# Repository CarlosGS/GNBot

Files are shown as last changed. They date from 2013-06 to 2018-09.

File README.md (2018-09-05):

GNBot: robotic platform for cooperative search strategies
=====

Low-cost 3D-printable robot design for testing cooperative search algorithms.  

**Check [the GNBot wiki page](https://github.com/carlosgs/GNBot/wiki) for more information**  

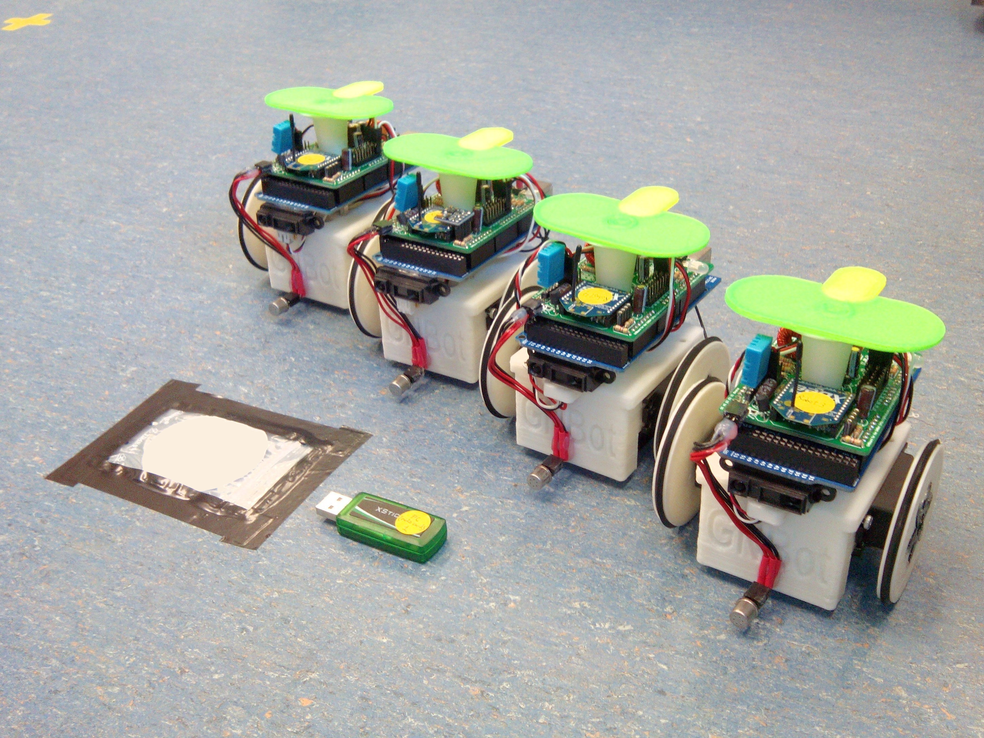
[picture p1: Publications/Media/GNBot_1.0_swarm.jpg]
  

The GNBot design allows the construction of a swarm of remotely-controlled robots that have multimodal sensory input (perceiving light, distance, temperature, humidity and orientation with an electronic compass) and are capable of detecting odor sources such as the low-profile target shown on the left.  

**Demonstration video of the swarm of GNBots used for Lévy-walk-based search:**
Demonstration video of the swarm of GNBots used for Levy-walk-based search (http://www.youtube.com/watch?v=HuAor0oZO_s)  

These robots are also energy efficient, open-source and easy to expand to allow the implementation of a great variety of cooperative search strategies (including those that use range information from each sensor modality with a characterization of the uncertainty of odor sources, and also the ones that use classical heuristic or brute-force approaches for search). Most importantly, the standardization of the platform could finally provide a fair base of comparison for evaluating differences in efficiency among these odor search strategies.  

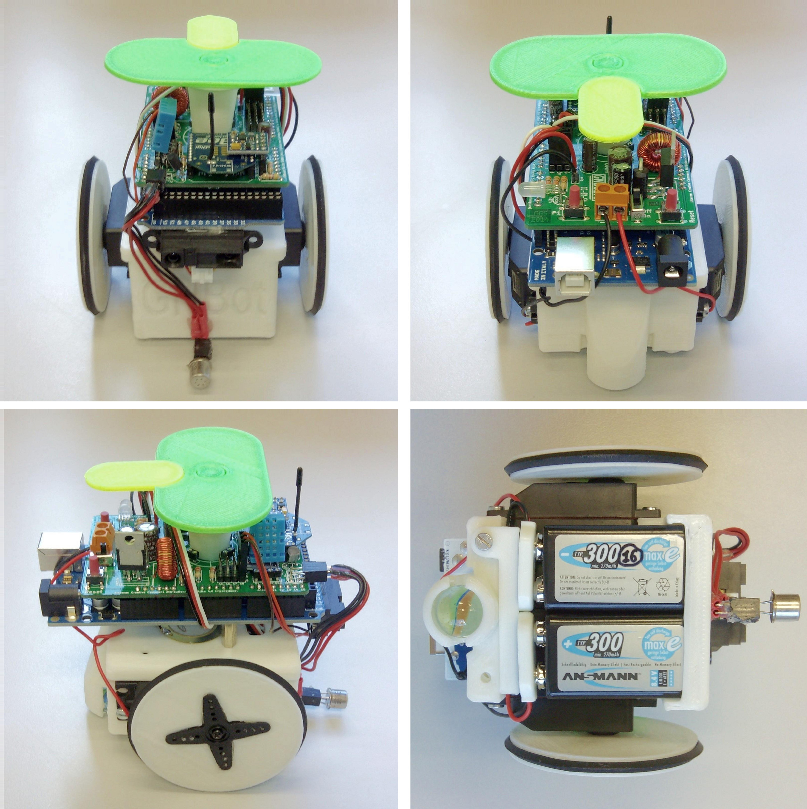
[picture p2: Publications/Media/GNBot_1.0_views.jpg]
  

List of sensors present in the robot:
TGS-2600 odor sensor, IR rangefinder, LDR light sensor array, electronic compass module, temperature and humidity sensors.
Battery voltage is also monitored.
The base actuators are two servomotors and the wireless interface is based on a ZigBee-compatible module.  

**Version 1.0:**  

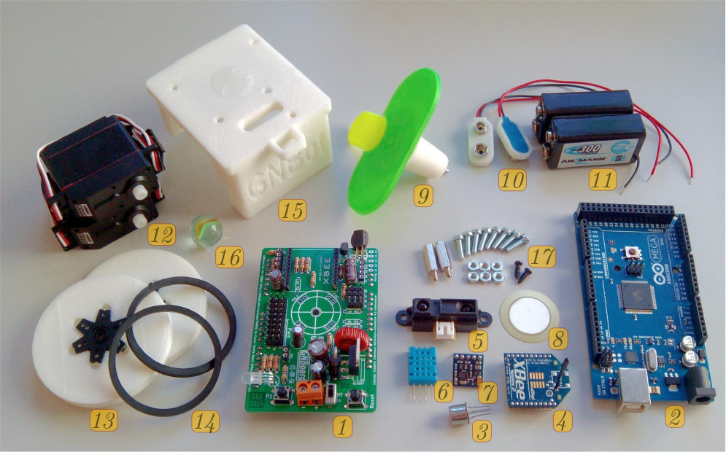
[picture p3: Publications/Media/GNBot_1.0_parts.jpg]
  

Items shown in the picture:
**1)** GNBoard electronics.
**2)** Arduino MEGA board.
**3)** TGS-2600 odor sensor.
**4)** ZigBee-compatible RF module.
**5)** Infra-red distance sensor.
**6)** DHT11 temperature and humidity sensor.
**7)** HMC5883L magnetometer sensor.
**8)** Piezoelectric buzzer.
**9)** Visual marker attachment.
**10)** Two 9V battery connectors.
**11)** Two 9V rechargeable batteries (300mAh).
**12)** Two continuous-rotation servomotors.
**13)** 3D-printed robot wheels.
**14)** Rubber outer-wheel rings.
**15)** 3D-printed GNBot chassis.
**16)** Marble for the idler wheel.  

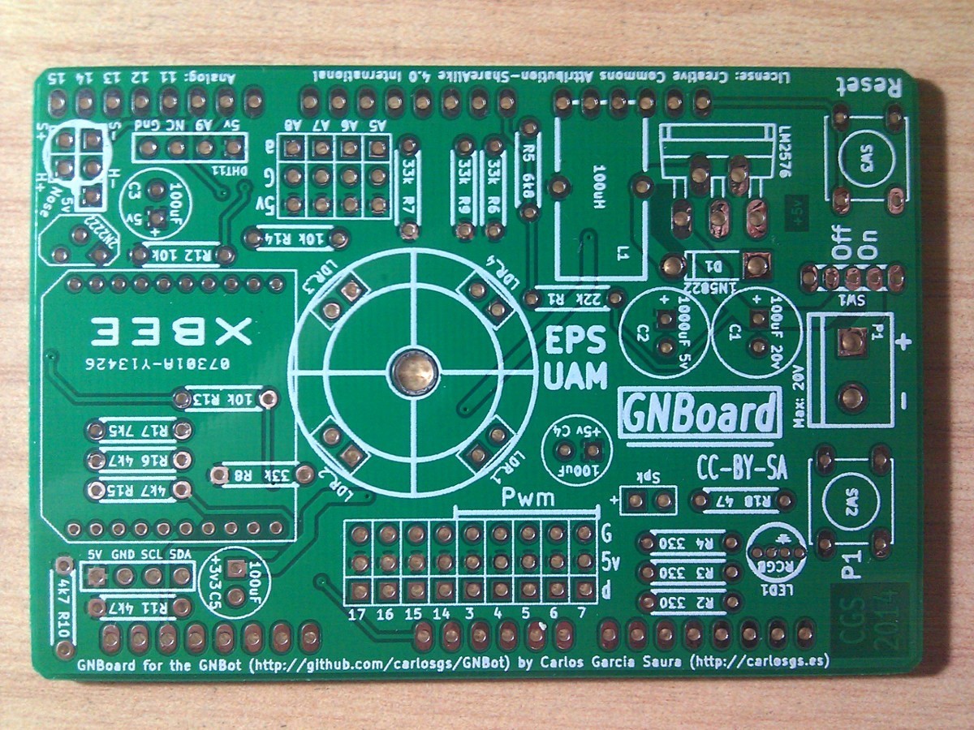
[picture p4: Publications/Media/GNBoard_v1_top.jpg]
  
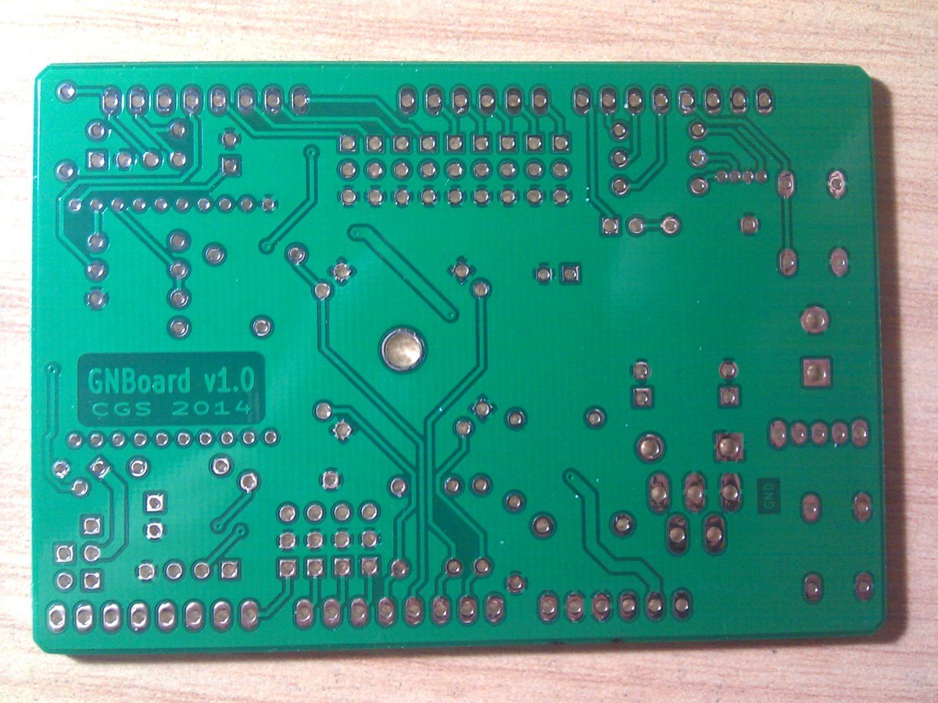
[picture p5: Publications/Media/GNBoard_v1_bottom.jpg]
  

**Version 1.0a:**  

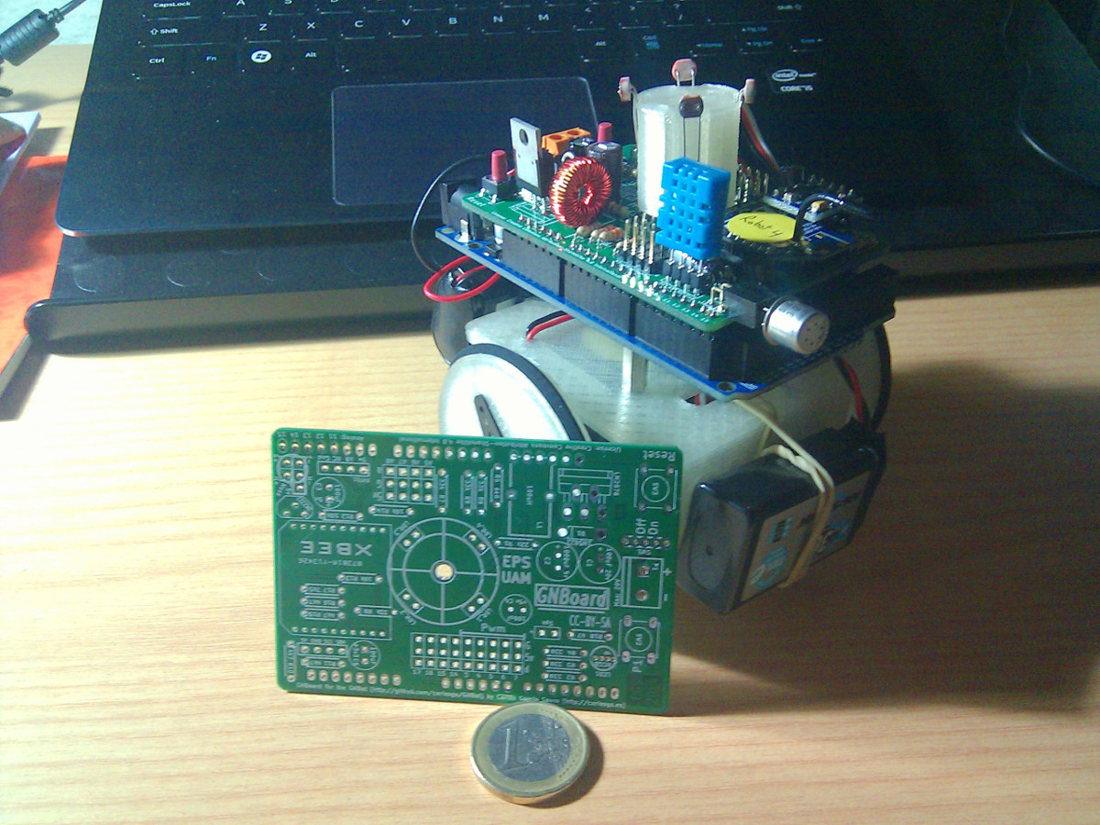
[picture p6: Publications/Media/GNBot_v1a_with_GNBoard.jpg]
  
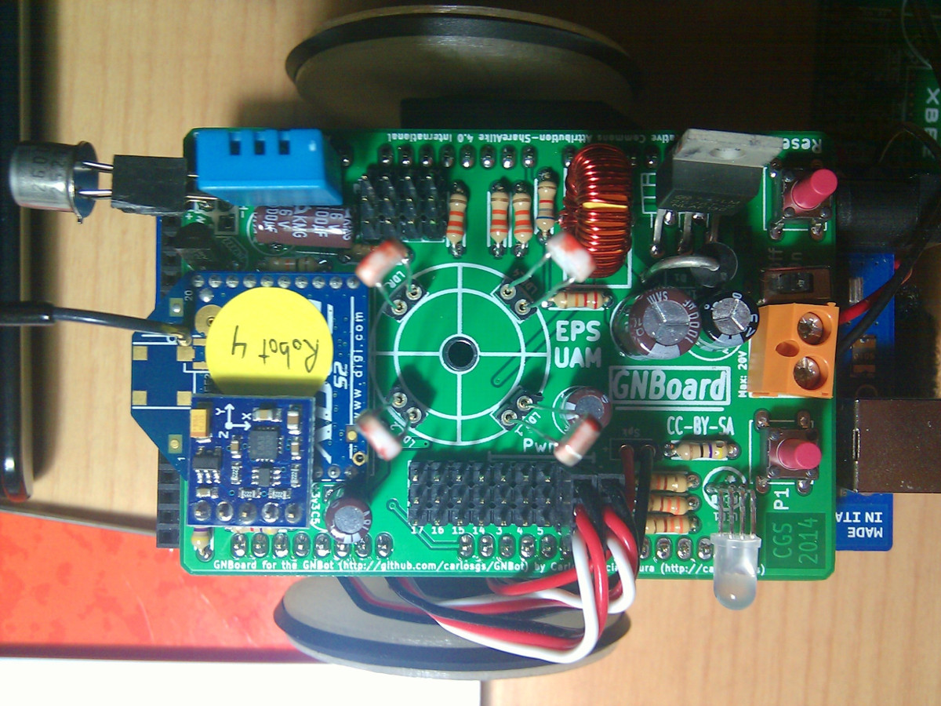
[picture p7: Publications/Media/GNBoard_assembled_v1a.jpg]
  

**Version 0.5:**  

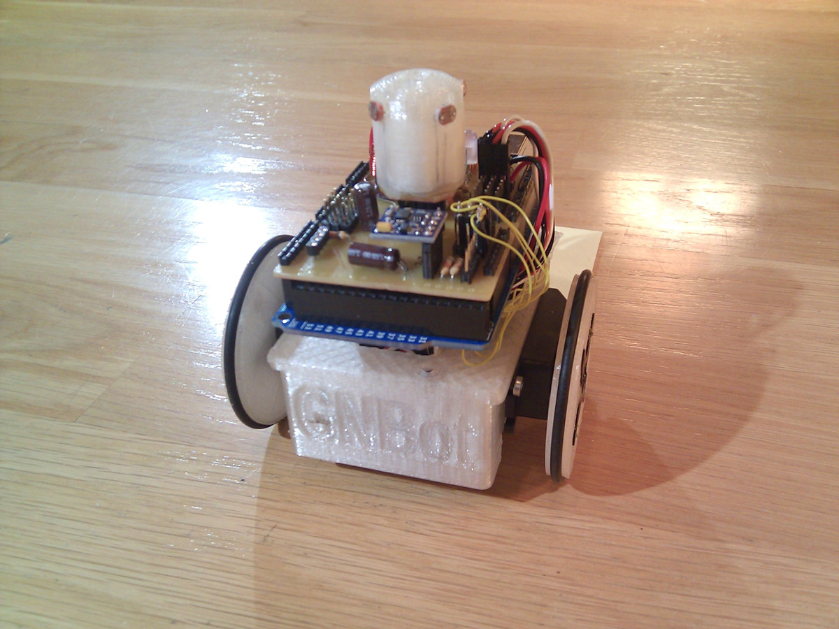
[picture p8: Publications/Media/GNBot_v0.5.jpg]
  

License  
--
License: **Attribution - Share Alike - Creative Commons (<http://creativecommons.org/licenses/by-sa/3.0/>)**  

Author:  
--
**@CarlosGS** <https://github.com/CarlosGS>

Disclaimer  
--
This hardware/software is provided "as is", and you use the hardware/software at your own risk. Under nocircumstances shall any author be liable for direct, indirect, special, incidental, or consequential damages resulting from the use, misuse, or inability to use this hardware/software, even if the authors have been advised of the possibility of such damages.

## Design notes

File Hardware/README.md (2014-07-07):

Hardware for the GNBot
=====

Designed derived from the ArduSkybot (whose origin was the MiniSkybot <http://www.iearobotics.com/wiki/index.php?title=Miniskybot_2>)

3d-printable robot design  
--

Regarding swarm robotics, printbots have been preferred over other solutions for both the reduced manufacture cost and, most importantly, for the high adaptability of the designs to the search problems. For instance, the use of 3D printed structures opens the possibility of easily testing the performance of various spatial distributions of the odor sensors in the robot, by manufacturing custom parts that can accommodate the different configurations.

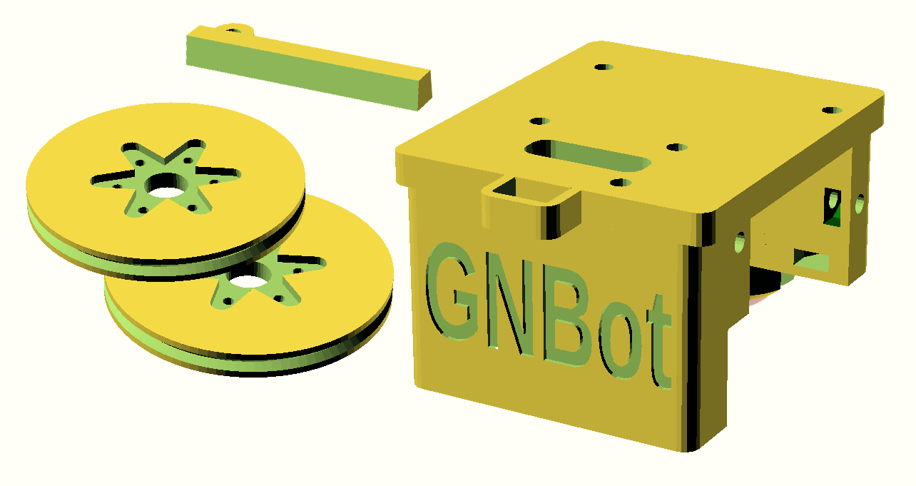
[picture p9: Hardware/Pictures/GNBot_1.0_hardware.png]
  

**Visual markers for video tracking with OpenCV**  
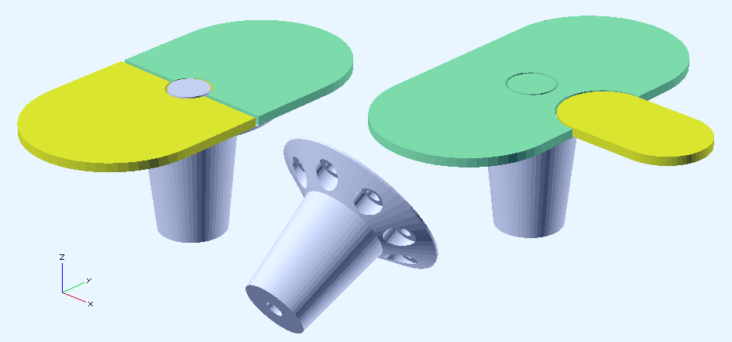
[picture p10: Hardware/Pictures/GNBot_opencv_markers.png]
  

License  
--
License: **Attribution - Share Alike - Creative Commons (<http://creativecommons.org/licenses/by-sa/3.0/>)**  

Author:  
--
**Carlosgs (<http://carlosgs.es>)**  

Disclaimer  
--
This hardware/software is provided "as is", and you use the hardware/software at your own risk. Under nocircumstances shall any author be liable for direct, indirect, special, incidental, or consequential damages resulting from the use, misuse, or inability to use this hardware/software, even if the authors have been advised of the possibility of such damages.

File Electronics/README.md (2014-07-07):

Electronics for the GNBot
=====

GNBoard shield for the Arduino MEGA  
--

An efficient solution for powering mobile robots. The GNBoard can also incorporate a ZigBee-compatible module and many other multimodal sensors (a gas detector for odor sensing, an accelerometer/electronic compass, temperature and humidity sensors, luminosity sensors), and multiple kinds of actuators as well (servomotors, a speaker, LEDs, etc).

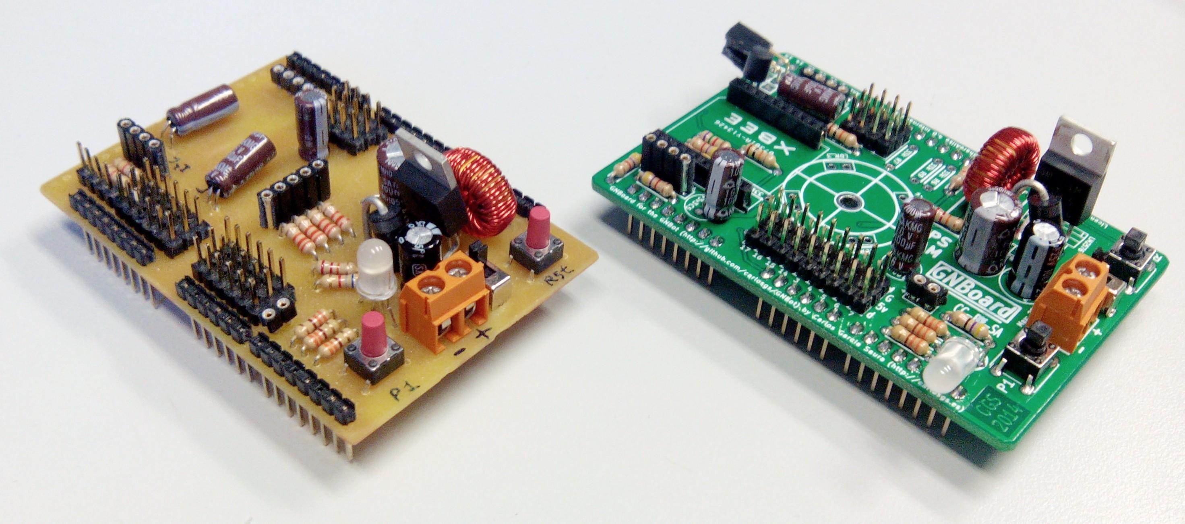
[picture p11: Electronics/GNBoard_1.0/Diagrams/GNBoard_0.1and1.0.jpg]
  
The two versions of the GNBoard developed for this project.
Prototype design (left) and version 1.0 (right).
The boards are designed to plug into an **Arduino MEGA**.  

The motion of the robot is achieved using two continuous rotation servomotors (**SM-S4303R**) as the main actuators. Servomotors provide a compact and low-cost solution to achieve the digital speed control needed.
The main downside of this kind of actuator is the high current demand -particularly during transient motions- which requires the use of an adequate power supply. For the GNBoard the design decision was to use a switching power supply rather than a linear regulator, provided the much higher efficiency.

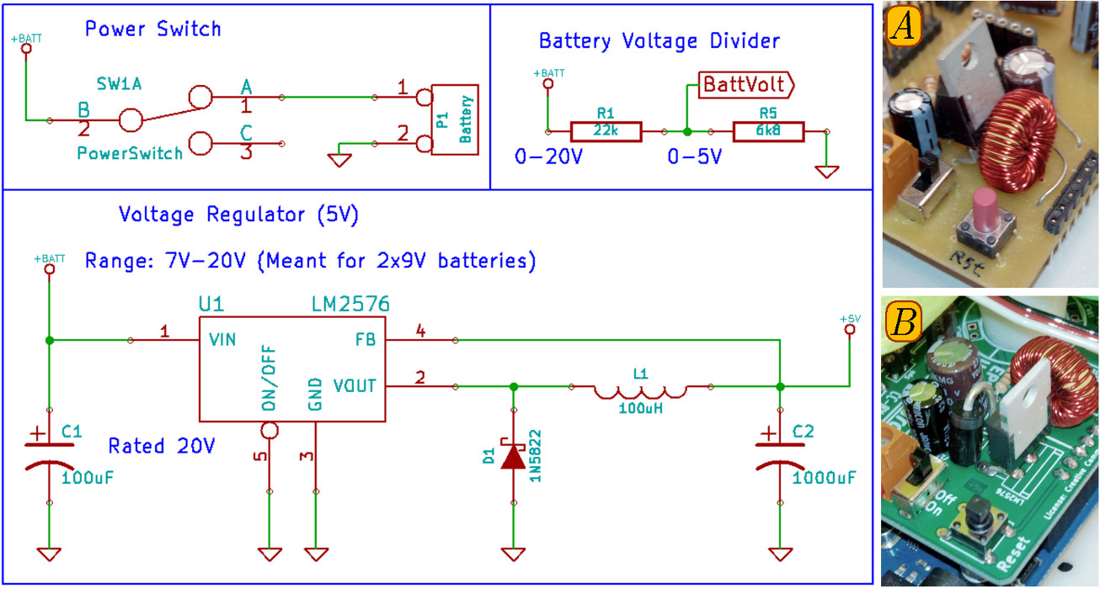
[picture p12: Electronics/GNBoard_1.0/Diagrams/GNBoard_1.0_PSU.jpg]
  
**Power supply schematic and actual assembly**
**A)** and **B)** respectively show the power supplies in GNBoard v0.1 and v1.0 (final version).
The power supply of the GNBoard uses an **LM2576-5** switching regulator that is capable of delivering up to 3A, which is more than sufficient to cover the energy demand of the entire robot.
Switching power regulators also have a broad input voltage range, allowing to make better use of the full capacity of the batteries since they can be connected in series without negative effect in the performance.

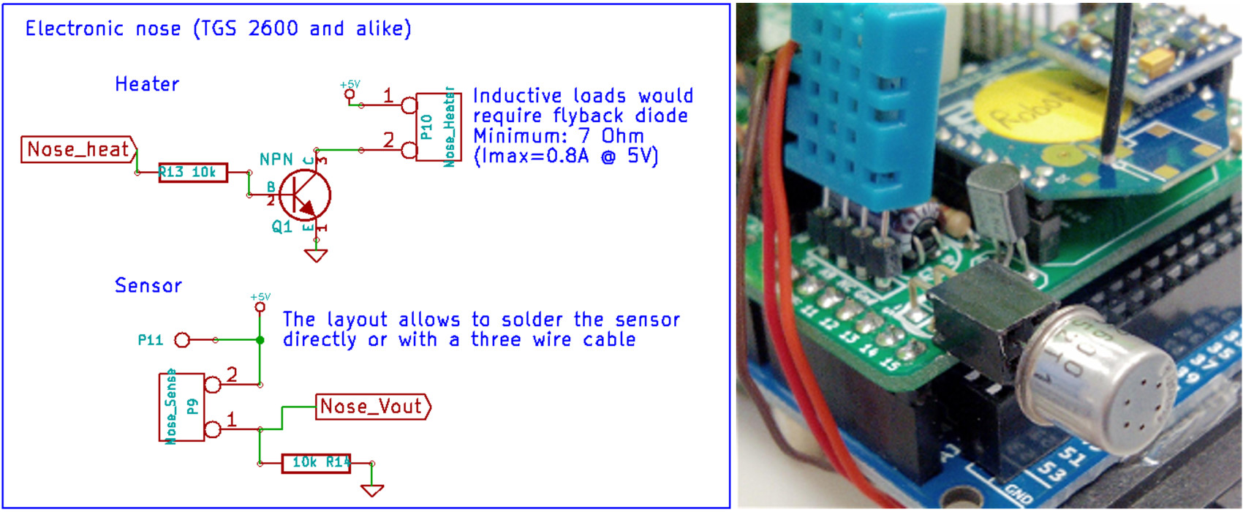
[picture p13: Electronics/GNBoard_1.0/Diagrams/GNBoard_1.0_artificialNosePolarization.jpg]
  
**Polarization scheme for the artificial nose sensor and detail picture of the assembly:**
The mounted sensor is the **TGS-2600** gas detector from <http://www.figarosensor.com/>, but any kind of sensor with a similar polarization scheme (as shown in the left panel) could be used.

Layout and schematics  
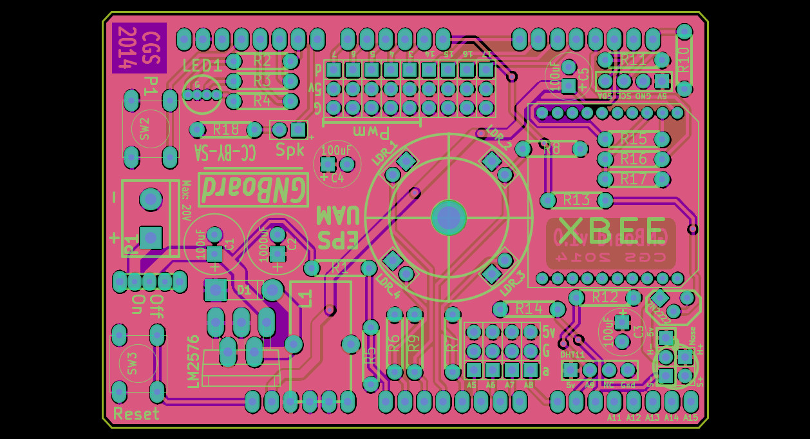
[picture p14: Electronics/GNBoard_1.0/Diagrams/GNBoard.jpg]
  
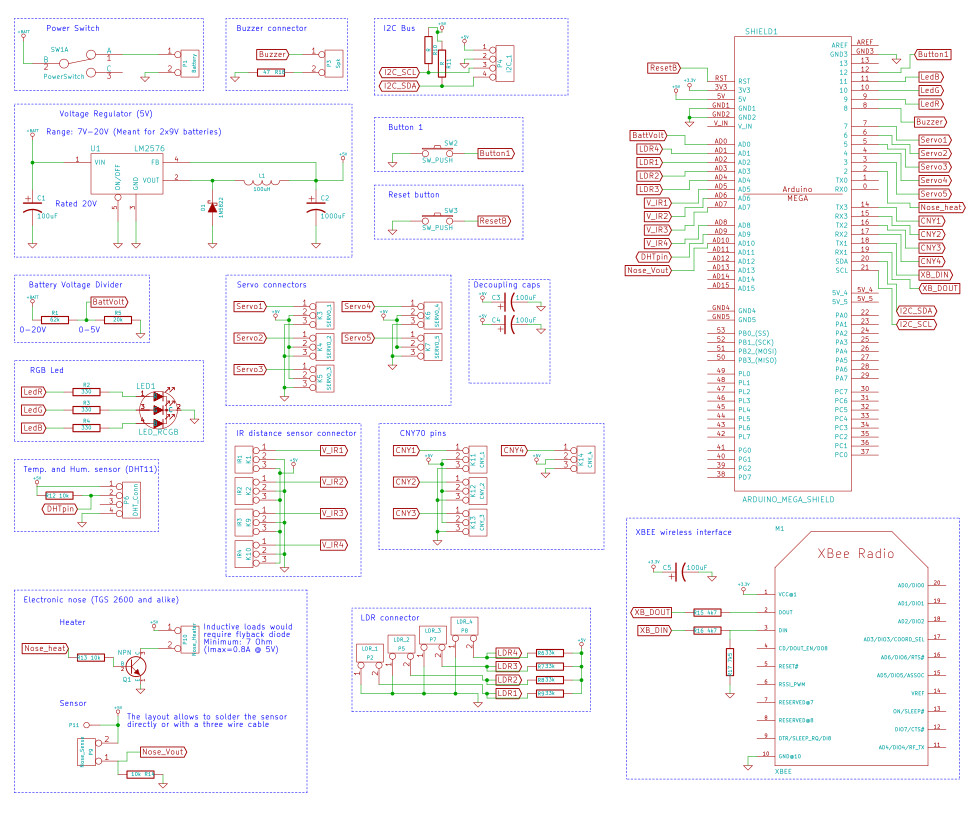
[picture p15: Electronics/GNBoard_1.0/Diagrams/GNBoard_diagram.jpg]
  
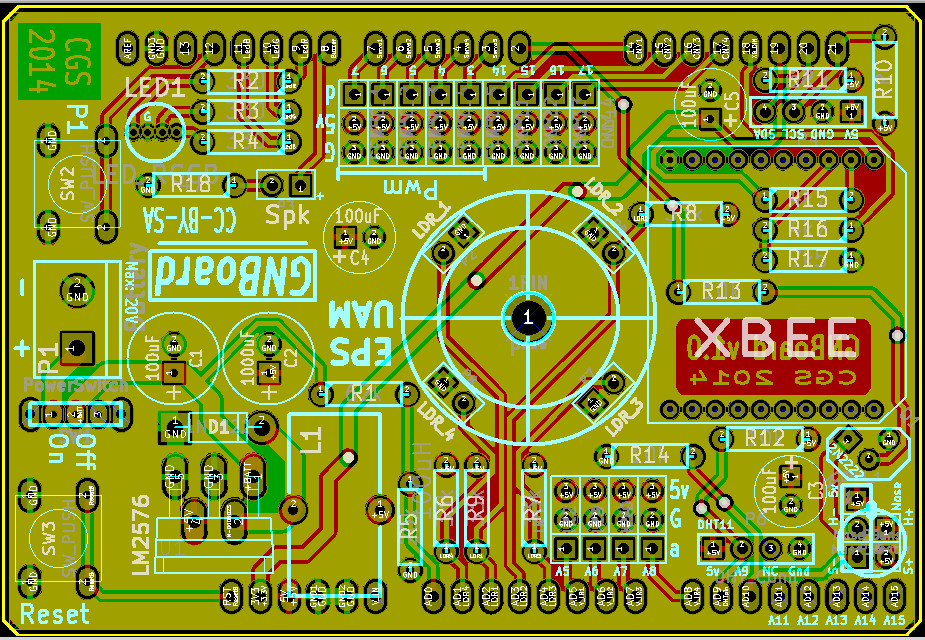
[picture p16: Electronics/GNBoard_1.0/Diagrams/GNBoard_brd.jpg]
  

License  
--
License: **Attribution - Share Alike - Creative Commons (<http://creativecommons.org/licenses/by-sa/3.0/>)**  

Author:  
--
**Carlosgs (<http://carlosgs.es>)**  

Disclaimer  
--
This hardware/software is provided "as is", and you use the hardware/software at your own risk. Under nocircumstances shall any author be liable for direct, indirect, special, incidental, or consequential damages resulting from the use, misuse, or inability to use this hardware/software, even if the authors have been advised of the possibility of such damages.

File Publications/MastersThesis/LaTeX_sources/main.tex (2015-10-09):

\documentclass[12pt,twoside]{report}

\usepackage{hyperref}
\hypersetup{
    hyperindex, linktoc=page, breaklinks,
    pdfauthor={Carlos Garcia-Saura},pdftitle={Self-calibration of a differential wheeled robot using only a gyroscope and a distance sensor}
}

\usepackage[utf8]{inputenc}
\usepackage{amsmath}
\usepackage{amsfonts}
\usepackage{amssymb}

\usepackage{setspace}

\usepackage{enumitem}

\usepackage[normalem]{ulem}

\usepackage[table,xcdraw]{xcolor}

%%%%%%%%%%%%%%%%%%%%%%%%%%%%%%%%%%%%%%%%%%%%%%%%%%%%%%%%%%%%%%%%%%%%%%%%%%%%%

% Definitions for the title page
\newcommand{\reporttitle}{Self-calibration of a differential wheeled robot using only a gyroscope and a distance sensor}
\newcommand{\reportauthor}{Carlos Garcia-Saura}
\newcommand{\supervisor}{Prof. Andrew J. Davison}
\newcommand{\degreetype}{Computing Science (Specialism in A.I.)}

\newcommand{\keywords}{Mobile robotics, differential wheeled robot, motion control, self-calibration, continuous-rotation servomotor, PID auto-tuning, multimodal sensing, MEMS gyroscope, IR distance sensor, open-source}

\setlength{\parskip}{\baselineskip}
\setlength{\parindent}{0pt}

%%%%%%%%%%%%%%%%%%%%%%%%%%%%%%%%%%%%%%%%%%%%%%%%%%%%%%%%%%%%%%%%%%%%%%%%%%%%%

% load some definitions and default packages
\input{includes}

\date{September 2015}

\begin{document}

% load title page
\input{titlepage}

\clearpage{\pagestyle{empty}\cleardoublepage}

% page numbering etc.
\pagenumbering{roman}
%\clearpage{\pagestyle{empty}\cleardoublepage}
\setcounter{page}{1}
\pagestyle{fancy}

%%%%%%%%%%%%%%%%%%%%%%%%%%%%%%%%%%%%
\begin{abstract}

Research in mobile robotics often demands platforms that have an adequate balance between cost and reliability. In the case of terrestrial robots, 
one of the available options is the GNBot, an open-hardware project intended for the evaluation of swarm search strategies.
The lack of basic odometry sensors such as wheel encoders had so far difficulted the implementation of an accurate high-level controller in this platform.
Thus, the aim of this thesis is to improve motion control in the GNBot by incorporating a gyroscope whilst maintaining the requisite of no wheel encoders.
Among the problems that have been tackled are: accurate in-place rotations, minimal drift during linear motions, and arc-performing functionality.
Additionally, the resulting controller is calibrated autonomously by using both the gyroscope module and the infrared rangefinder on board each robot, greatly simplifying the calibration of large swarms.
The report first explains the design decisions that were made in order to implement the self-calibration routine, and then evaluates the performance of the new motion controller by means of off-line video tracking. The motion accuracy of the new controller is also compared with the previously existing solution in an odor search experiment.

\textbf{Keywords:} \emph{\keywords}
\end{abstract}

\clearpage{\pagestyle{empty}\cleardoublepage}
%%%%%%%%%%%%%%%%%%%%%%%%%%%%%%%%%%%%
\section*{Acknowledgements}
\emph{In first place I must thank professor Andrew J. Davison at Imperial College London for his patient guidance and for pointing this project in the right direction.
I found the Robotics course to be very inspiring so I want to thank as well the rest of coordinators and course assistants.}

\emph{I am also thankful to professors Pablo Varona and Francisco de Borja Rodr\'iguez at Universidad Aut\'onoma de Madrid, for allowing me to use their infrastructure to perform the experiments. My friends Alejandro, Irene and Aar\'on also deserve a mention for making the research time in the lab (and outside the lab!) way more enjoyable.}

\emph{From the great people I have met this year at Imperial College London, I want to mention in special Hadeel, Bob, Matthew, Stefan, Marta, \sout{Dony}Doniyor, Pawel, Tony, Siwook, Yui, and Win for always being there, for the good and the bad, no matter how complicated the assignment or big the cake! :-)
I must mention as well the IC Robotics Society and IC Advanced Hackspace, in special Larissa and Audrey for helping a lot with the 3D printers and laser cutters.
Also, my year in London wouldn't have been the same without yOPERO, Erin, Charlaine, Christian and Cliona.}

\emph{I also want to thank the whole open-source community (specially GNU/Linux, Python, Numpy, Matplotlib, OpenCV, Arduino, RepRap, etc) for making it possible to perform this project without requiring any proprietary software or machinery.}

\emph{Finally, big thanks go to my parents for their continuous loving support, and also thanks to Rodrigo, FJ and Sandra for tolerating my mood swings while working in this project during our family holidays.}

\emph{!`Muchas gracias a todos!}

\emph{-- Carlos}

\clearpage{\pagestyle{empty}\cleardoublepage}

%%%%%%%%%%%%%%%%%%%%%%%%%%%%%%%%%%%%
%--- table of contents
\fancyhead[LE,RO]{\slshape}
\fancyhead[RE,LO]{\sffamily {Table of Contents}}

\begin{spacing}{0.1}
\tableofcontents 
\end{spacing}

\clearpage{\pagestyle{empty}\cleardoublepage}

\fancyhead[RE,LO]{\sffamily {List of Figures}}

\begin{spacing}{0.1}
\listoffigures
\end{spacing}

\clearpage{\pagestyle{empty}\cleardoublepage}
\pagenumbering{arabic}
\setcounter{page}{1}

\fancyhead[LE,RO]{\slshape}
%\fancyhead[LE,RO]{\slshape \rightmark}
\fancyhead[LO,RE]{\slshape \leftmark}

%%%%%%%%%%%%%%%%%%%%%%%%%%%%%%%%%%%%
\chapter{Introduction}

The starting point of this project is the \emph{GNBot} swarm robot platform that was presented in \emph{``Design principles for cooperative robots with uncertainty-aware and resource-wise adaptive behavior''}\cite{GarciaSauraLM14}, and \emph{``Cooperative strategies for the detection and localization of odorants with robots and artificial noses''}\cite{GarciaSaura14}.
Figure \ref{fig:GNBotViews} describes the most relevant characteristics of these robots.

\begin{figure}[hbtp]
\centerline{
}
\caption[One of the robots from the GNBot swarm used for the project]{\emph{One of the robots from the GNBot swarm used for the project.}
The electronics are based on the Arduino MEGA board. A custom shield contains all of the multimodal sensors, which provide the robot with gas sensing capabilities (TGS-2900), as well as distance sensing (GP2Y0A21YK0F), temperature \& humidity (DHT11), and light intensity sensing.
\textbf{This project additionally incorporated a gyroscope module (MPU6050)}.
The main actuators are two continuous-rotation servomotors, and each robot also has a multicolor RGB LED and a piezoelectric speaker.
Finally, the wireless communication layer is based on ZigBee, and the green/yellow top markers allow for external video tracking of the swarm.
From \cite{GarciaSauraLM14,GarciaSaura14}.
}
\label{fig:GNBotViews}
\end{figure}

The GNBot is a \emph{differential wheeled robot}, which means that it has two active wheels sharing the same axis, and each of them is actuated independently. There is also a passive, free turning ball caster that acts as a third stand. If the desired trajectory is a straight path, the velocities are set to equal magnitude; if a rotation is required instead, then different velocities can be applied to each motor.

Using this setup it is possible to estimate the motion of the robot in the XY plane given its starting position ($P_{xy\alpha}$), the rotational velocity of each motor ($\omega_L$, $\omega_R$), the diameter of the wheels ($D_L$, $D_R$) and their separation ($d$). This estimation process is known as \emph{dead reckoning}\footnote{\url{https://en.wikipedia.org/wiki/Dead_reckoning}}.

The accuracy of dead reckoning relies on how dependable the measurements used in the calculations are. These include wheel separation and their diameter, but most importantly the actual rotational velocities of each motor.
For instance, small deviations from the theoretical velocities can turn a desirably linear trajectory into an arc. An example of this issue is displayed in Figure \ref{fig:levyDriftSingle}.

\begin{figure}[hbtp]
\centerline{
}
\caption[Example of an odor search strategy based on L\'{e}vy walks, as performed by the original robot controller]{\emph{Example of an odor search strategy based on L\'{e}vy walks, as performed by the original robot controller.}
The search is defined at a high level as random in-place rotations combined with linear trajectories whose lengths vary according to a heavy-tailed probabilistic distribution. \textbf{It can be appreciated that the segments that were supposed to be linear, are actually performed as arcs (there is drift in yaw)}.
In this experiment, the target odor source (red marker) took 12 minutes to be found.
The ground truth trajectory was recorded with a webcam, post perspective correction and color marker tracking with the OpenCV software library.}
\label{fig:levyDriftSingle}
\end{figure}

\pagebreak

This thesis has tackled the improvement of those low-level control routines in order to minimize motion drift, as well as the implementation of a distance-based abstraction layer that facilitates the use of the GNBot platform in practical applications.
It also explores the automatic calibration of the robots using only on-board sensors (a gyroscope and a distance sensor).

The following two sections are an overview of the project's approach towards the improvement the motion controller; Chapter \ref{sec:calib_chap} provides an in-depth explanation of the self-calibration algorithm; Next, Chapter \ref{sec:eval_chap} evaluates the resulting controller; Finally, Chapter \ref{sec:concl_chap} analyses the outcome of the project and suggests future research paths.

\section{Background and motivation} \label{sec:bg_section}

Undesired drift in the estimation of position, very characteristic when using dead reckoning in mobile robotics, can be reduced with the incorporation of basic \emph{odometry}\footnote{\emph{Odometry:} Use of sensory data to improve motion estimates} such as \emph{rotational encoders}\footnote{\emph{Rotational encoder:} A sensor that can measure wheel rotations accurately and in real time}.
Wheel encoders are a very common choice given their simplicity and reduced cost, but they do have some drawbacks:
\begin{itemize}[noitemsep,topsep=0pt,parsep=5pt,partopsep=0pt]
\item Incorporating wheel encoders into a previously existing design is often nontrivial, as the process involves hardware modifications  near critical moving parts.
\item Electrical, optical or magnetic wheel encoders can be susceptible to dirt; placing them near the wheels may make periodic maintenance necessary.
\item Most importantly, wheel encoders cannot easily detect whether there is any slipping between the wheel and the ground surface.
\end{itemize}

For these reasons the incorporation of wheel encoders in the GNBot has been dismissed.
Instead, the first trials towards the reduction of yaw drift included the use of an electronic compass. The goal was to obtain a global, unbiased measure of heading (yaw) by measuring the earth's magnetic field. Unfortunately the compass was deemed unusable for indoor environments during the first trials of the GNBot\cite{GarciaSaura14}, since the magnetometer measurements are substantially distorted by nearby metals (i.e. buried cables) commonly present indoors.

Another option for odometry is the gyroscope, which is the approach studied in this project (see Fig. \ref{fig:GNBotGyro}). Electronic gyroscopes are a form of inertial sensor that can measure relative rotations in any orientation, without requiring interactions with external moving parts. As opposed to wheel encoders, the physical incorporation of a gyroscope into the GNBot would be quite straightforward, and would also have the advantage of being capable of easily detecting wheel slipping.

\begin{figure}[hbtp]
\centerline{
}
\caption[Detail of the gyroscope module installed in the GNBot]{\emph{Detail of the gyroscope module installed in the GNBot.} The selected board is based on the MPU6050 module, which is Arduino-compatible. The module fits on the $I^2C$ socket of the GNBot without any additional modification.
An orange wire was soldered to the interrupt pin, but it was not needed in the end, as polling was used to read values from the module.
}
\label{fig:GNBotGyro}
\end{figure}

The use of inertial sensors for position estimation has been a matter of research for many decades. The last few years in particular have seen the development of smartphones, tablets, intelligent cameras and other devices in need of inertial sensors, which has greatly boosted the industry. The technology has been able to achieve high miniaturization, high accuracy and low power consumption, whilst substantially reducing costs, yielding the excellent inertial sensors that are now widely available in the market.

In robotics, Inertial Measurement Units (IMUs) are quite often employed for navigation in different environments.
For instance, the combination of IMUs with GPS allows for a remarkably accurate 3D localization in aerial robotics\cite{Barczyk10}. These techniques have also been demonstrated in ground robots without GPS\cite{PeiChunLin06,SeungbeomWoo11}, as well as in underwater robots without encoders\cite{Stilwell01,Kinsey02,Panish11}.
More recently, 3D position tracking with inertial sensors has also been employed to correct the effect of the rolling shutter of RGB\cite{HyoungKiLee12} and RGB-D\cite{Ovren13} camera sensors.

Many authors use \emph{Kalman filters}\footnote{\url{https://en.wikipedia.org/wiki/Kalman_filter}} in their motion controllers. Kalman filtering is a probabilistic method for sensor fusion, which means it can be used to efficiently combine measurements from the inertial sensor with other forms of odometry such as wheel encoders, a compass, or even barometers; this way it is possible to achieve very robust motion controllers with minimal drift\cite{PeiChunLin06,HyoungKiLee12,
HakyoungChung01,panich11}.
In fact, most of the commercially-available IMUs, such as the one selected for this project, already contain internal Kalman filters that can integrate measurements from a gyroscope, an accelerometer or a compass.

For the final evaluation of the positioning accuracy of the controller, the project took advice from work by J. Borenstein et al.\cite{HakyoungChung01,Borenstein98}, where the robots were programmed to describe square trajectories that were first logged and then compared against ground truth.

%Self calibration (SLAM):
%\cite{DeCecco02} % inertial + odometry
%\cite{roy99}
%\cite{martinelli07}

%kalman
%\cite{HakyoungChung01,PeiChunLin06,
%HyoungKiLee12,martinelli07,panich11}

%Gyro. Square for evaluation:
%\cite{Borenstein98,HakyoungChung01}

%3D navigation (including accelerometers):
%Inertial navigation systems:
%Hexapod:
%\cite{PeiChunLin06}
%UAV aided by GPS:
%\cite{Barczyk10}
%Linear velocity calibration using Fuzzy %inference:
%\cite{SeungbeomWoo11}

%Monocular SLAM:
%\cite{HyoungKiLee12}

%RGB-D rolling shutter:
%\cite{Ovren13}

%Gyro. Underwater:
%\cite{Stilwell01,Kinsey02,Panish11}

%Gyro. Kalman filter
%\cite{panich11}

\section{Contribution overview}

At the start of this project, the motion control of the GNBot robots was speed-based and open-loop (with no wheel encoders). This resulted in very inaccurate motions that drifted rapidly from the desired path. For example, when a robot was commanded to describe a straight trajectory, an arc path would be observed instead. In-place rotations were also quite inaccurate.

Thus the goal of this project has been to improve the motion accuracy of these robots and to provide a high-level distance-based controller.
In particular the following matters have been tackled:

\begin{itemize}
\item Incorporation of an inertial sensor (MPU6050) into the GNBot design, as well as the implementation of low-level functionality that reads \emph{yaw, pitch and roll} from the gyroscope module with minimal drift.
\item Analysis of the servomotor response curves. Since there are no wheel encoders, the rotations were tracked using the gyroscope, by independently rotating each wheel over the entire range of velocities.
\item Implementation of a PID controller for accurate yaw regulation; Additionally the constants are auto-calibrated with a process based on the Ziegler-Nichols method.
\item Analysis of the infrared sensor response curve, and linearisation using exponential curve fitting.
\item Analysis of the nonlinear effect of the PID yaw controller over the robot's linear velocity for the whole range.
\item The results of these analysis have been integrated into a high-level distance-based motion controller that supports linear motions and arcs. Additionally, the calibration of each robot is done autonomously by using only on-board sensors (the gyroscope and the IR rangefinder) and requiring minimal user interaction.
\item Implementation of an off-line video tracking method capable of reliably recording ground truth robot paths. The process involved perspective \& distance correction using the OpenCV library.
\item Evaluation of the new controller by making the robots perform lines, circles and squares of known dimensions; Also the system was compared against the previously existing solution in an odor search task based on a wall-bounce strategy.
\end{itemize}

The new motion controller has a linear drift in the order of $6cm/m$ in the low velocity settings ($2$ to $6cm/s$) and around $9cm/m$ at higher velocities ($6$ to $10cm/s$). The rotational drift is in the order of $2deg/min$ when the robot is moving.

In summary, this project has provided the high-level functionality needed in order to achieve accurate control over the GNBot robots. The self-calibrating nature of the approach also facilitates its use in large robot swarms.

The outcome of the project is open-source (Attribution-ShareAlike 4.0 International\footnote{\url{http://creativecommons.org/licenses/by-sa/4.0/}}) and can be accessed in the following GitHub respository:

\begin{center}
\large\url{https://github.com/carlosgs/GNBot}
\end{center}

%%%%%%%%%%%%%%%%%%%%%%%%%%%%%%%%%%%%
\chapter{The self-calibration algorithm} \label{sec:calib_chap}

The original controller on-board the GNBot was velocity-based and its input units were arbitrary -- it did not have an internal mapping between the motor's inputs and real-world units (i.e. $cm/s$). It was also lacking methods for basic calibration, in part due to the absence of any form of odometry. Altogether, these facts lead to large amounts of drift.
Far from being a constant that could have been compensated by basic calibration, drift varied with the velocity of the robots -not only in magnitude but also in direction-, so straightforward calibration was not an option (see Figure \ref{fig:gnbotLinearDrift}).
This project has tackled the problem by incorporating a gyroscope for odometry. The advantages of this approach in contrast with the use of wheel encoders were already discussed in Section \ref{sec:bg_section}.

The selected \emph{Inertial Measurement Unit} (IMU) is the MPU6050\footnote{\url{http://www.invensense.com/products/motion-tracking/6-axis/mpu-6050/}} chip, which is based on MEMS technology (Micro-Electro-Mechanical Systems). It is commonly available as an Arduino-compatible break-out board that conveniently fits on the $I^2C$ socket of the GNBot without any additional modifications (c.f. Figure \ref{fig:GNBotGyro}).

The gyroscope module has the same $I^2C$ pinout as the magnetometer that was originally present in the robot, but the routines that handle both modules are very different. In fact, the example code for the inertial sensor (a part of the \emph{$I^2C$ Device Library}\footnote{\url{http://www.i2cdevlib.com/devices/mpu6050}}) depends on the use of hardware \emph{interruptions}\footnote{\emph{Interrupt:} Signal to the processor indicating that some event needs immediate attention} rather than \emph{polling}\footnote{\emph{Polling:} As opposed to interruptions, polling actively samples the status of an external device}.
The use of interruptions was highly undesirable since the main processor needs to handle time sensitive tasks such as sensing and radio communications as well as motion control, so the gyroscope library was modified to use a polling scheme.

The MPU6050 incorporates a \emph{Digital Motion Processor} (DMP) that can be used to offload computations from the robot's main processor. These computations include the task of filtering and integrating the raw values from the on-chip acceleration sensors, in order to output ready to use \emph{yaw, pitch and roll}. In the GNBot controller the raw values are sampled and processed at $200Hz$ by the DMP co-processor.

The gyroscope module also has an internal FIFO\footnote{\emph{FIFO:} ``First In First Out'' queuing policy} buffer that allows for reliable high-frequency data readings (up to $200Hz$), though in this project it was deemed unnecessary since the sample rate is low ($<50Hz$). Once the IMU had been incorporated into the GNBot, it was possible to read the \emph{yaw, pitch and roll} of the robot back into the computer (see Figure \ref{fig:gnbotLinearDrift}).

\begin{figure}[hbtp]
\centerline{
}
\caption[Initial experiments to analyse drift in the original controller]{\emph{Initial experiments to analyse drift in the original controller.} The robot was commanded to describe a straight path by setting both motors to the same velocity during 3 seconds.
The trajectory (upper panel) was recorded with a ceiling camera for three different velocities, while yaw (lower panel) was being logged using the on-board gyroscope.
It can be observed that drift is accurately tracked by the empirical yaw measurements.
The input speed setting is arbitrary since both continuous-rotation servomotors are commanded with the built-in $Servo.write([degrees])$ functions from the Arduino IDE, which do not have a direct mapping with real world velocities.
}
\label{fig:gnbotLinearDrift}
\end{figure}

At this point, a basic proportional yaw controller was implemented in order to demonstrate the viability of the system. The controller could now successfully correct the direction of the robot so it followed a straight path, even after external perturbations had been applied (i.e. rotating the robot or placing obstacles).

With those results as a motivation, the design of a high-level self-calibrating motion controller was tackled. An overview of the resulting calibration routine is shown in Figure \ref{fig:full_calibration_procedure} -- Further sections will describe the technical details in greater depth.

\begin{figure}[hbtp]
\centerline{}
\caption[Full self-calibration procedure]{\emph{Full self-calibration procedure.} \textbf{\textit{(a)}} The robot is first placed in front of a wall, and remains static while the gyro drift is compensated, \textbf{\textit{(b)}} The minimum motion threshold is found by gradually increasing the input of each motor until a rotation is perceived \textbf{\textit{(c)}} The motors are then independently run at their maximum speed setting in order to record the corresponding real-world rotational velocity, \textbf{\textit{(d)}} Next, the yaw PID controller is heuristically calibrated by analysing the oscillations for different parameters, \textbf{\textit{(e)}} Finally, the robot uses the distance sensor to measure its approach velocity towards the wall, creating a map between the input values ($rad/s$) and the resulting real-world linear velocity ($cm/s$).\\
Technical details can be found in sections: $(a)$ \ref{sec:gyro_section}, $(b$ \& $c)$ \ref{sec:rotVel_section}, $(d)$ \ref{sec:PID_section}, $(e)$ \ref{sec:linearVel_section}.
}
\label{fig:full_calibration_procedure}
\end{figure}

\newpage
\section{Minimization of gyroscope drift} \label{sec:gyro_section}

Most electronic gyroscopes calculate rotational magnitudes by integrating measurements from rotational accelerometers over time.
Ideally this integration process would consistently yield the same outputs when a sequence of rotations is applied, but instead, rotational accelerometers often have inaccuracies (i.e. bias, sensitivity limits, variability with temperature, etc.) that cause \emph{drift} in the integration process.
This would imply for instance that the yaw measurement of a static robot would erroneously vary over time.

Gyroscope drift is often minimized with either a proper calibration of the accelerometer bias, with signal filtering or by pausing the integration process while no motion is detected. Fortunately, the DMP co-processor of the MPU6050 already implements these features very efficiently (see Fig. \ref{fig:gyro_drift}).

In order to measure yaw drift rate (whose units are \emph{degrees per minute}) it was necessary to differentiate the yaw measurements provided by the gyroscope (\emph{radian} units). This was achieved by accurately timing distinct yaw measurements with the function \emph{millis()} from Arduino\footnote{\url{https://www.arduino.cc/en/Reference/Millis}}.
\begin{equation}
drift\_rate=\frac{yaw(t_2)-yaw(t_1)}{t_2-t_1}\cdot\frac{180 deg}{\pi rad}\cdot\frac{1 min}{60 s}deg/min
\end{equation}

\vspace{-5mm}

\begin{figure}[hbtp]
\centerline{
}
\caption[Analysis of gyroscope drift (with static robot)]{\emph{Analysis of gyroscope drift (with static robot).} The gyroscope has an initial transient that must be respected, during which the internal DMP (Digital Motion Processor) performs self-calibration to account for drift. The module is fully calibrated after 23 seconds of the robot being static, when drift becomes inferior to 0.5 deg/min (step A in Fig. \ref{fig:full_calibration_procedure}). It must be noted though that the magnitude of this drift will not be constant, but is instead greatly affected by the robot's motions.
}
\label{fig:gyro_drift}
\end{figure}

\section{Calibration of the motors} \label{sec:rotVel_section}

This section tackles the calibration of the continuous-rotation servomotors, which are actuators that generate a rotational velocity that is proportional to a PWM input signal (Pulse Width Modulation).
The relationship between the input and output magnitudes is arbitrary, so a real-world mapping needs to be learned first.

To better understand the calibration process it helps to be familiar with the following notation:

\begin{figure}[hbtp]
\centerline{
}
\caption[Diagram of the robot's top view, displaying the notation used]{\emph{Diagram of the robot's top view, displaying the notation used.}
The grey arrow points towards the front of the robot.
$D_L$ and $D_R$ are the wheel diameters, and $d$ is their separation. $V_L$ and $V_R$ are the contributions of each motor to the robot's linear velocity, and $\alpha$ is the yaw measurement (positive for clockwise rotations).
}
\label{fig:robot_diagram_notation}
\end{figure}

Most mobile robotic platforms have encoders that simplify the calibration process by measuring the real-world rotational velocities of the wheels. In the case of the GNBot there are no wheel encoders, so a different approach was needed.

The implemented method can measure the response curve of each motor independently by using only the gyroscope. This process is described in Figure \ref{fig:speed_calib_diagram}.

\begin{figure}[hbtp]
\centerline{
}
\caption[Method employed to measure $\omega_R$, the contribution of the right motor to the robot's rotational velocity $\omega$.]{\emph{Method employed to measure $\omega_R$, the contribution of the right motor to the robot's rotational velocity $\omega$.}
A constant velocity is first applied to the right wheel ($V_R=C$) while the left wheel is fixed ($V_L=0$).
This results in a rotation of the robot around the ground-contact point of the left wheel. The gyroscope is then used to measure the rotational velocity $\omega_R=\omega$.
Afterwards the same process is repeated for the left motor.
This method allows to separately evaluate the response curves of each motor without requiring wheel encoders.
}
\label{fig:speed_calib_diagram}
\end{figure}

The angular velocity $\omega$, directly measured by the gyroscope, is coupled with the rotational speed of both motors with constants $K_L$ \& $K_R$, that account for $D_L$, $D_R$ (wheel diameters), and $d$ (distance between wheels).
Using this technique it was possible to record the response curve of each motor by independently performing a sweep over the full range of velocity inputs.
The result is shown in Figure \ref{fig:velocity_response_curve}.

\begin{figure}[hbtp]
\centerline{
}
\caption[Measured motor response curves]{\emph{Measured motor response curves.}
The panels show the response curves of the left (red) and right (blue) motors for different wheel sizes.
The input of the continuous-rotation servomotors is PWM (Pulse Width Modulation), and the output ($\omega$) is the rotational rate of the robot around its vertical axis (the setup is described in Fig. \ref{fig:speed_calib_diagram}).
Each trial was run for a single motor at a time, and the sweep took around 30 seconds per motor.
Three regions can be appreciated: a flat \emph{dead-zone} ($\omega=0rad/s$), a linear response region ($0 < \omega < 1.5rad/s$), and saturation ($\omega \geq 1.5rad/s$, which has been highlighted in red).
For the same wheel size -middle panel- the L/R response curves are almost identical.
Robots with larger left or right wheels -left \& right panels- instead have visibly different L/R response curves.
The calibration routine implemented in this project accounts for these differences.
}
\label{fig:velocity_response_curve}
\end{figure}

Self-calibration of these curves has been implemented by means of linear fitting between the minimum and maximum velocities within the linear region. In first place, the robot measures the \emph{dead-zone} of a motor (the minimum motion threshold) by gradually increasing its input velocity until a rotation is perceived. Then, the maximum velocity is measured by running the motor at the maximum speed setting within the linear range (PWM$\approx$1300 or PWM$\approx$1650).
These measurements are performed for the forward and backward directions of each motor (steps B \& C in Fig. \ref{fig:full_calibration_procedure}).

The left and right motors contribute to the robot's global angular velocity $\omega$ in an additive manner ($\omega=\omega_L+\omega_R$, i.e. setting $\omega_L=0.5rad/s$ and $\omega_R=0.5rad/s$ yields $\omega=1.0rad/s$).
Knowing this fact, and using the data from Figure \ref{fig:velocity_response_curve}, it was possible to determine the input region that corresponds to a linear motion. This is when both rotational contributions cancel out so the robot does not rotate: $\omega=\omega_L+\omega_R=0rad/s \rightarrow \omega_L=-\omega_R$.
This region is represented in Figure \ref{fig:linear_trajectory_PWM_mapping}.

\begin{figure}[hbtp]
\centerline{
}
\caption[Region of motor input values that correspond to a linear trajectory]{\emph{Region of motor input values that correspond to a linear trajectory.}
The red and green data points are from robots with larger left or right wheels respectively, while the blue data points are from a robot with identical wheels. It can be observed that each of these curves has a different steepness: a greater slope indicates that the right motor needs to rotate faster in order to account for a larger left wheel, and vice-versa.
}
\label{fig:linear_trajectory_PWM_mapping}
\end{figure}

\section{PID auto-tuning using the Ziegler-Nichols method} \label{sec:PID_section}

At this point a basic motor controller had been implemented, so the rotational rate ($rad/s$) of the robot could be accurately commanded. Closed-loop yaw control was now possible with the implementation of a PID regulator (Proportional-Integral-Derivative) that combines the  motor controller with real-time gyroscope measurements (Eqn. 2.2). The error measure is calculated as $e(t)=yaw_{target}-yaw(t)$.
\begin{equation}
output\_rotation\_rate(t) = K_p e(t) + K_i \int_{0}^{t}e(\tau)d\tau + K_d \frac{d}{dt}e\ \ [rad/s]
\end{equation}

A PID controller is based on user-tunable gains ($K_p$, $K_i$ \& $K_d$) that, when properly adjusted, can minimize the overshoot of the transient response; in the case of the GNBot, the PID is the responsible of achieving fast and accurate changes in yaw. This is represented in Figure \ref{fig:P_controller_vs_autotuned_PID}.

\begin{figure}[hbtp]
\centerline{}
\vspace{-3mm}
\centerline{}
\caption[Response of the yaw controller to a step function and to a sinusoid]{\emph{Response of the yaw controller to a step function (upper panel) and to a sinusoid (lower panel).}
The controller was commanded with time-varying yaw targets while the transitions were recorded using the gyroscope.
It can be appreciated that a proportional controller either is too slow (cyan curve), has over-shoot (blue curve) or even ripple (red curve).
The auto-tuned PID (green curve) does have some overshoot as well, but it is a much better approximation to the ideal response.
}
\label{fig:P_controller_vs_autotuned_PID}
\end{figure}

Rather than manually specifying a fixed parameter set for the PID, this project tackled the self-calibration of the controller with the popular technique proposed by Ziegler and Nichols\cite{ziegler1942optimum}. This heuristic tuning method is performed by setting the three gains ($K_p$, $K_i$ \& $K_d$) to zero, and then increasing the proportional term $K_p$ until it reaches the ultimate gain $K_u$ at which the controller presents self-sustained oscillations of period $T_u$.
Ziegler and Nichols (ZN) then provide with the mapping between $K_u$ \& $T_u$ and the three gains of the PID controller.
In this project the modified tuning values proposed by Tyreus and Luyben\cite{luyben1997essentials} were used instead as they increased the robustness of the controller. Table 2.1 compares the gain specifications of both tuning methods.

\begin{table}[hbtp]
\centering
\begin{tabular}{l|l|l|l|}
\cline{2-4}
                                                              & \cellcolor[HTML]{EFEFEF}$K_p$ & \cellcolor[HTML]{EFEFEF}$t_I$ & \cellcolor[HTML]{EFEFEF}$t_D$ \\ \hline
\multicolumn{1}{|l|}{\cellcolor[HTML]{EFEFEF}Ziegler-Nichols (ZN)} & $K_u/1.7$                     & $T_u/2$                       & $T_u/8$                       \\ \hline
\multicolumn{1}{|l|}{\cellcolor[HTML]{EFEFEF}Tyreus-Luyben (TLC)}   & $K_u/2.2$                     & $2.2T_u$                      & $T_u/6.3$                     \\ \hline
\end{tabular}
\caption{\emph{Prescribed PID gain values for the Ziegler-Nichols (ZN) \& Tyreus-Luyben (TLC) heuristic tuning methods.}
Compared to the original values proposed by Ziegler \& Nichols, the TLC rules tend to reduce the oscillatory effects and improve the robustness of the yaw controller.
The $t_I$ and $t_D$ values were converted into the standard PID form using $K_i = K_p/T_i$ and $K_d = K_pT_d$.
}
\label{my-label}
\end{table}

In order to provide a consistent PID calibration, the parameters $K_u$ -ultimate gain- and $T_u$ -oscillation period- needed to be measured accurately and reliably. An automated method was implemented for this purpose (see Figure \ref{fig:PID_auto_tuning}).

\begin{figure}[hbtp]
\centerline{
}
\caption[PID auto-tuning process: Empirical measure of the values $K_u$ \& $T_u$]{\emph{PID auto-tuning process: Empirical measure of the values $K_u$ \& $T_u$.}
The tuning is done as follows: In first place, $K_i$ \& $K_d$ are set to zero, and $K_p$ is set to a very large value that ensures oscillation (the value is such that the maximum motor speed is applied at 1 degree of error). Next, the proportional controller is perturbed by setting a 45 degree angle as the target yaw. Then the algorithm checks whether the oscillation is self-sustained, in which case it updates $K_p=K_p/1.5$. This process is repeated until the oscillations become attenuated; at that point $K_u$ \& $T_u$ are finally registered (step D in Fig. \ref{fig:full_calibration_procedure}).
}
\label{fig:PID_auto_tuning}
\end{figure}

\section{Mapping rotational velocities with linear motions} \label{sec:linearVel_section}

Using the basic motion controller it was now possible to command the robot to perform linear trajectories quite accurately; but the inputs units were still rotational magnitudes related to yaw ($\omega_L$ \& $\omega_R$ $[rad/s]$). The next step was to create a mapping between these inputs and the real-world linear velocities of the robot (i.e. $cm/s$).

In first place it was necessary to have a method that could accurately measure the robot's motions.
External tracking systems (i.e. VICON\footnote{\url{http://www.vicon.com/products/camera-systems}} or a ceiling camera) are among the best solutions available for this purpose, but they were deemed too sophisticated to be incorporated into the basic calibration routine. These methods were employed for the final evaluation of the motion controller instead (Chapter \ref{sec:eval_chap}).

Rather than requiring an external tracking system, the problem of measuring the robot's real-world velocity has been tackled with the use of the distance sensor on-board the GNBot.
The sensor is the \emph{Sharp GP2Y0A21YK0F}\footnote{\url{http://www.sharpsma.com/optoelectronics/sensors/distance-measuring-sensors/GP2Y0A21YK0F}} infrared rangefinder, and it has the voltage response curve analysed in Figure \ref{fig:IR_sensor_response_curve_B}.

\begin{figure}[hbtp]
\centerline{
}
\caption[Analysis of the response curve of the infrared distance sensor]{\emph{Analysis of the response curve of the infrared distance sensor.}
The figure displays the output voltage of the \emph{Sharp GP2Y0A21YK0F} rangefinder and its variability with the distance between the sensor and a wall. Manufacturer specifications rate this module for distance measurements in the range $10cm<d<80cm$, and indeed it can be appreciated that the response outside that region is either flat ($d>80cm$) or nonlinear ($d<10cm$, highlighted in red).
}
\label{fig:IR_sensor_response_curve_B}
\end{figure}

The approach undertaken towards the calibration of linear motions was the use of the IR distance sensor on-board the GNBot to achieve accurate real-world velocity measurements. Theoretically, the robot would be driven towards a wall at a constant speed, and then the robot's velocity could be calculated by differentiating distance measurements over time.

In order to achieve a fair degree of resolution in these measurements, the output of the IR sensor needed to be calibrated first by means of linearisation. The method is introduced in Figure \ref{fig:IR_sensor_response_curve}.

\begin{figure}[hbtp]
\centerline{
}
\caption[Linearisation of the IR rangefinder sensor response]{\emph{Linearisation of the IR rangefinder sensor response.}
The left panel shows the response curves that were recorded for three different GP2Y0A21YK0F distance sensors (red, green and blue curves).
These curves were fitted with an exponential decay (cyan curve) in the range of highest sensitivity ($10cm<d<40cm$).
The right panel evaluates the accuracy of the fitted model, showing a maximum theoretical deviation of $\approx3cm$.
}
\label{fig:IR_sensor_response_curve}
\end{figure}

The fitting function in Figure \ref{fig:IR_sensor_response_curve} is an inverse function with two fitting parameters $K$=$21.6V/cm$ \& $C$=$0.16V$ that were calculated using two data points located in the limits of the highest sensitivity range ($d_1$=$10cm$ \& $d_2$=$40cm$), using the following equations:
\begin{equation}
v_{fit}(d)=K\cdot\frac{1}{d}+C \ \ \ \rightarrow\ \ \ 
K = d_1\frac{v(d_1)-v(d_2)}{1-\frac{d_1}{d_2}} \ \ \ \ \ \ 
C = v(d_2)-\frac{K}{d_2}
\end{equation}
The calibration of the IR distance sensor is \emph{not} a part of the self-calibration routine since it requires user interaction; instead, the fitting curve can be generalised to every robot that uses the GP2Y0A21YK0F sensor model.

This newly-calibrated distance sensing functionality was verified to work within the theoretically-calculated tolerances for different wall surfaces.
Having this infrastructure in place, the problem of linear velocity calibration could finally be tackled.
For this purpose, the GNBot was commanded to move towards a wall at different velocities while yaw was corrected by the closed-loop PID controller. The real-world linear approach velocity ($v\ cm/s$) was then recorded for multiple input velocity settings ($\omega_c\ rad/s$), yielding the results shown in Figure \ref{fig:linear_velocity_calibration_curves}.

\begin{figure}[hbtp]
\centerline{
}
\caption[Linear velocity calibration for two different ground surfaces]{\emph{Linear velocity calibration for two different ground surfaces.}
The panels show how the real-world velocity of the robot varies over its input range, for both backward and forward motions (red and blue curves) and for two different ground surfaces (left and right panels).
The green and magenta dashed lines represent a linear fitting of the velocity response of each material.
It can be appreciated that the speed of the robot over foam (right panel) is lower for the same input values; this is due to friction effects.
Friction also causes an asymmetry in the velocity responses for backward and forward motions; this is because the robot is not perfectly symmetric.
The nonlinear region is a cause of the PID operating the motors outside their linear range (c.f. Fig. \ref{fig:velocity_response_curve});
such effect could be minimized with velocity-dependent PID gains.
}
\label{fig:linear_velocity_calibration_curves}
\end{figure}

Self-calibration was then implemented by means of a linear fitting that measures the real-world velocity at the highest velocity setting within the linear region. This measurement is performed four times and then averaged (step E in Fig. \ref{fig:full_calibration_procedure}), being the last step of the self-calibration process.
Each of the calibration parameters are then stored into the non-volatile EEPROM memory built into the Arduino, so the tuning process is not required every time the robots are powered on.

Finally, high-level distance-based control was implemented by integrating over time the current velocity setting; this way the robot can stop whenever a specified distance has been reached. This is a very simple method that does not account for transients in velocity.
Arc functionality was implemented by interpolating the target yaw throughout a distance-based motion; specifying different initial/final yaw angles effectively converts a linear segment into an arc.

%%%%%%%%%%%%%%%%%%%%%%%%%%%%%%%%%%%%
\chapter{Evaluation of the motion controller} \label{sec:eval_chap}

The purpose of the controller described in Chapter \ref{sec:calib_chap} is to provide accurate high-level motion control for the GNBot robots.
This chapter evaluates the real-world performance of this controller.

In first place, a series of experiments were designed in order to be able to measure the different \emph{motion drift} characteristics. For instance, the robots would be commanded to perform squares and circles of known dimensions while external video tracking provided unbiased measurements of the actual trajectories. 
The tracking process is described in Figures \ref{fig:perspective_correction} and \ref{fig:opencv_tracking_steps}.

\begin{figure}[hbtp]
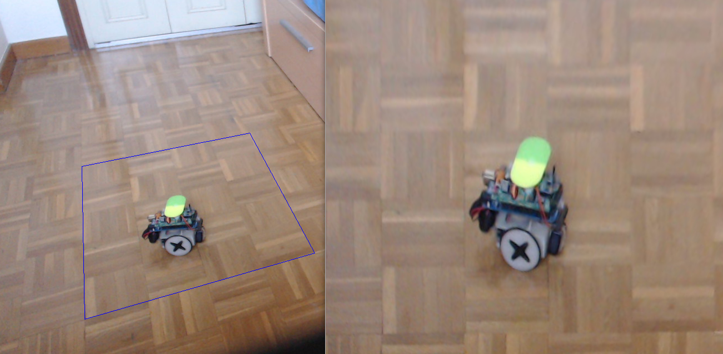
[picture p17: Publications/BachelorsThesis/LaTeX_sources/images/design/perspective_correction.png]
\centerline{}
\caption[Perspective correction for accurate video tracking]{\emph{Perspective correction for accurate video tracking.}
The video tracking system was calibrated using perspective correction with a square of known dimensions. This allows for a 1:1 mapping between image units and real-world distances in the XY plane. 
}
\label{fig:perspective_correction}
\end{figure}

\begin{figure}[hbtp]
\centerline{}
\caption[How color markers are tracked with the OpenCV library]{\emph{How color markers are tracked with the OpenCV library.}
In first place the reference points for perspective correction need to be specified by using the cursor \emph{(1)}. Next, the marker color is selected \emph{(2)}, and then a threshold is applied \emph{(3)}. The algorithm finally looks for the largest blob, which yields the coordinates of the robot \emph{(4)}. From \cite{GarciaSaura14}.
}
\label{fig:opencv_tracking_steps}
\end{figure}

Using this tracking system it was possible to record the trajectories of each robot with a very high resolution. Next sections describes the experiments that were performed.

\vspace{-5mm}

\section{The effect of gyroscope drift} \label{sec:sect31}

\vspace{-5mm}

Though gyroscope drift is always compensated upon the initialization of the GNBots, such compensation is far from ideal, and as a consequence the robot's motions present yaw drift over time. This effect is analysed in Figure \ref{fig:cumulative_yaw_error}.

\begin{figure}[hbtp]
\centerline{}
\vspace{-2.5mm}
\caption[Cumulative yaw error due to gyroscope drift]{\emph{Cumulative yaw error due to gyroscope drift.}
In this experiment, the robot was commanded to repeat a linear trajectory multiple times (alternating the target yaw between $0^{\circ}$ and $180^{\circ}$) for both forward motion (red path) and backward motion (green path)
at a velocity setting of $5cm/s$.
Using this data, the rotational drift of the controller has been calculated to be in the order of $2\ deg/min$ in a moving robot.
}
\label{fig:cumulative_yaw_error}
\end{figure}

\section{Analysis of linear positioning accuracy} \label{sec:sect32}

Next, the general performance of the distance-based controller was evaluated by first commanding the robots to perform squares and circles and then comparing the results against ground-truth dimensions.
Square trajectories were implemented with straight line segments interleaved with in-place rotations of $90^{\circ}$. This functionality yielded the results shown in Figure \ref{fig:square_distance_comparison}.

\begin{figure}[hbtp]
\centerline{}
\caption[Evaluation of the linear accuracy of the distance-based controller]{\emph{Evaluation of the linear accuracy of the distance-based controller.}
A GNBot robot (lower-right corner) was commanded to describe square trajectories of different sizes while its path was recorded using the vision-based method described in Figures \ref{fig:perspective_correction} \& \ref{fig:opencv_tracking_steps}.
The red path corresponds to a purposely-miscalibrated robot (it was calibrated with a different set of wheels).
The cyan and magenta paths correspond to robots with different wheel sizes that were properly self-calibrated.
Finally, the green path corresponds to a self-calibrated robot with same wheel diameters.
Linear drift has been calculated to be around $3cm/m$. This was done by scaling up the maximum deviation from the lower-left corner of the largest square trajectory -- about $1.5\ cm$ for the calibrated robots.
It can be appreciated that the shape of the squares is correctly maintained thanks to the gyroscope -which is always calibrated upon start up-, and the square dimensions only fall out of the specification for the miscalibrated robot (red path).
}
\label{fig:square_distance_comparison}
\end{figure}

In order to simplify the video tracking process, measurements were conducted in one single continuous experiment for each robot. In the case of square trajectories, the GNBot would perform the different square sizes one after another -- without an intermediate re-positioning of the robot.
This generated an undesired drift in the starting position of each trial, which made manual alignment necessary.
The post processing consisted in a affine translation from the starting points to the origin ($x,y$=$0,0$) and posterior re-setting of the initial yaw angle by means of a global rotation.
This process effectively removed the effects of yaw drift between each trial (the effect had already been analysed in Figure \ref{fig:cumulative_yaw_error}).

Circular motions were implemented with the arc functionality, by setting the initial and final arc angles to $0^{\circ}$ and $360^{\circ}$. Path length was calculated as $l$=$2 \pi r$.
This approach yielded the results shown in Figure \ref{fig:circle_distance_comparison}.

\begin{figure}[hbtp]
\centerline{}
\caption[Evaluation of the accuracy of arcs performed by the controller]{\emph{Evaluation of the accuracy of arcs performed by the controller.}
A GNBot robot (lower-right corner) was commanded to describe circular trajectories of different sizes while its path was recorded.
The cyan and magenta paths correspond to robots with different wheel sizes that were properly self-calibrated.
The green path corresponds to a self-calibrated robot with same wheel diameters.
Finally, the red path corresponds to a different robot that was also self-calibrated.
The maximum drift from ground-truth diameters is around $8cm/m$, though it can be appreciated that the circular shape is correctly maintained thanks to the gyroscope
(which is always calibrated upon start-up).

}
\label{fig:circle_distance_comparison}
\end{figure}

\newpage
\section{How velocity affects the controller} \label{sec:sect33}

The implemented motion controller relies on the integration of velocities over time for its distance estimations.
In Section 2.4 it was observed that there is a nonlinear region in the velocity response curves (c.f. Figure \ref{fig:linear_velocity_calibration_curves}). Since these responses are linearly fitted, the use of velocities outside the linear range will result in inaccurate distance estimations. The effect of velocity is analysed in Figures \ref{fig:square_velocity_comparison} \& \ref{fig:circle_velocity_comparison}.

\begin{figure}[hbtp]
\centerline{}
\caption[Effect of velocity in the repeatability of square trajectories]{\emph{Effect of velocity in the repeatability of square trajectories.}
The setup of these trials is similar to the one in Figure \ref{fig:square_distance_comparison}, but in this case the size of the squares were set to a constant $l$=$30cm$ and performed at different speeds.
The maximum drift is in the order of $6cm/m$ in the low velocity settings ($2$ to $6cm/s$) and around $9cm/m$ at higher velocities ($6$ to $10cm/s$).
}
\label{fig:square_velocity_comparison}
\end{figure}

\begin{figure}[hbtp]
\centerline{}
\caption[Effect of velocity in the repeatability of circular trajectories]{\emph{Effect of velocity in the repeatability of circular trajectories.}
The setup of these trials is similar to the one in Figure \ref{fig:circle_distance_comparison}, but in this case the circle diameters were set to a constant $D$=$30cm$ and performed at different speeds.
The maximum drift in diameter is around $7cm/m$ in the low velocity settings ($2$ to $6cm/s$) and around $8.5cm/m$ at higher velocities ($6$ to $10cm/s$).
}
\label{fig:circle_velocity_comparison}
\end{figure}

\newpage
\section{Performance in odor search experiments}

The GNBot robots were originally designed as a platform that could evaluate swarm search strategies in real-world environments\cite{GarciaSauraLM14,GarciaSaura14}. The target of those searches are odor sources based on volatile compounds (such as ethanol) that can be detected by the gas sensor on-board each robot.

Among the search strategies that have been so far evaluated with this platform are L\'{e}vy-based search (c.f. Fig. \ref{fig:levyDriftSingle}) and wall-bounce search.
Unfortunately, at the time of those trials a calibrated motion controller was not yet present. This fact caused great uncertainty in the evaluation process: the calculated motion commands for a particular search were not being faithfully reproduced by the swarm.

Some of those experiments have been re-run for this project -- this time using the self-calibrated motion controller in order to evaluate the improvement. Trials were performed in the seminar room shown in Figure \ref{fig:experiments_room}.

\begin{figure}[hbtp]
\centerline{}
\caption[Room used for the odor search experiments]{\emph{Room used for the odor search experiments.} The odor search experiments required an effective area of approximately $16m^2$, an indoors environment free of disturbances and with uniform light conditions that facilitate video tracking.
Chairs were moved to the back of the room, and the search arena was installed in the center (blue walls). Air conditioning was turned off during the experiments on order to minimize air currents. The robot swarm can be seen on top of the table, as well as the computer used to record tracking data.
}
\label{fig:experiments_room}
\end{figure}

Wall-bounce search is a very primitive form of search where a robot is commanded to maintain a constant velocity until either an obstacle or the target are encountered; for obstacles, the robot must rotate away and continue with a different heading.
The simplicity of the wall-bounce strategy makes it very sensible to the linearity of the robot's motions. For instance, a robot with enough yaw drift may rotate in circles  over the same area without ever finding any obstacle that modifies its path. Given its sensitivity to drift, wall-bounce search is a very good candidate for the comparison of both motion controllers.
The experimental setup is described in Figure \ref{fig:search_experiment_setup}.

\begin{figure}[hbtp]
\centerline{}
\caption[Setup of a wall-bounce search experiment (conducted with the new motion controller)]{\emph{Setup of a wall-bounce search experiment (conducted with the new motion controller).}
The upper panel shows the starting robot positions, as well as the location of the odor targets. These are based on cotton pads impregnated with ethanol. The lower panel shows an overlay of the search path described by each robot.
It can be appreciated that the trajectories are accurately performed as lines, which faithfully matches the high-level definition of the wall-bounce algorithm.
}
\label{fig:search_experiment_setup}
\end{figure}

The results of these search experiments are further discussed in the next section.

%%%%%%%%%%%%%%%%%%%%%%%%%%%%%%%%%%%%
\chapter{Conclusions} \label{sec:concl_chap}

This thesis has tackled the improvement of the motion controller on board the GNBot by incorporating gyroscope-based odometry that does not require wheel encoders.
The outcome is a high-level controller that can faithfully perform in-place rotations, arcs, and linear trajectories. This controller is calibrated, so its inputs are real-world units (centimeters and degrees). Additionally this calibration process is automatic and uses only two on-board sensing capabilities: the gyroscope and the distance sensor.

The general approach of the project has been to separately analyse the sources of motion uncertainty, and then try to find ways to minimise them (i.e. by observing a response curve and working only within its linear region). Many of the error sources could not be separated, so the calibration process had to progressively build a layered confidence base, which in the end allowed for complete self-calibration:

\vspace{-3.5mm}

\begin{itemize}
\item In first place, the output of the gyroscope (the MPU6050 inertial sensor) was analysed. It was found that the yaw measurement varied over time even when the robot was static, so this drift had to be compensated (Section \ref{sec:gyro_section}).
\item Then the response curves of the motors were analysed using the calibrated gyroscope. This was done by activating a single motor at a time and measuring the rotational velocities of the robot (c.f. Fig. \ref{fig:speed_calib_diagram}). The response curves were plotted for robots with different wheel diameters (c.f. Fig. \ref{fig:velocity_response_curve}). These were then linearised, which allowed control over real-world units of rotational speed (Section \ref{sec:rotVel_section}).
\item Using the calibrated motor functions, a PID yaw controller was implemented and tested in order to guarantee accurate yaw control (c.f. Fig. \ref{fig:P_controller_vs_autotuned_PID}). This allowed for fast and accurate yaw transitions. It also allowed for very accurate closed-loop linear trajectories (Section \ref{sec:PID_section}).
\item The IR distance sensor on-board the GNBot (Sharp GP2Y0A21YK0F) was then evaluated and linearised (c.f. Figs. \ref{fig:IR_sensor_response_curve_B} \& \ref{fig:IR_sensor_response_curve}).
Finally, the PID yaw controller was used in combination with the distance sensing capability in order to perform accurate velocity measurements. This way it was possible to measure the \emph{linear velocity response curves} of the robot (c.f. Fig. \ref{fig:linear_velocity_calibration_curves}). Basic fitting allowed for accurate velocity-based control with real-world input units (Section \ref{sec:linearVel_section}).
\end{itemize}

\vspace{-5mm}

The self-calibration process that has been implemented (c.f. Fig. \ref{fig:full_calibration_procedure}) uses only the gyroscope and distance sensors on board the GNBot to automatically measure all the necessary parameters, without requiring any user interaction. The process simply requires manual placement of the robot in front of a wall, and takes approximately 92 seconds.

Video tracking was used for the evaluation of the controller's accuracy (Chapter \ref{sec:eval_chap}). Tracking was implemented using the OpenCV library, first performing perspective correction, and then identifying the position of the color marker by applying a threshold (c.f. Figs \ref{fig:perspective_correction} \& \ref{fig:opencv_tracking_steps}). This tracking method was used to compare the new controller with the previously existing solution, in a wall-bounce odor search experiment (see Figure \ref{fig:wallBounce_oldVSnew}).

\begin{figure}[hbtp]
\centerline{}
\caption[Comparison of a ``Wall bounce'' search using the original controller and the new self-calibration]{\emph{Comparison of a ``Wall bounce'' search using the original controller (left) and the new self-calibration (right).}
The figure shows the trajectories of four GNBot robots in two different odor search experiments. The starting positions are represented with triangle markers
and the targets are represented as squares.
It can be appreciated that the original controller (left panel) has large amounts of yaw drift. The new controller (right panel) faithfully matches the theoretical definition of wall-bounce search.
}
\label{fig:wallBounce_oldVSnew}
\end{figure}

The tracking method also allowed to measure the effect of \emph{gyroscope drift} (by having the robot repeatedly perform straight lines, as seen in Section \ref{sec:sect31}), the \emph{linear positioning accuracy} (by performing squares and circles of different sizes, as seen in Section \ref{sec:sect32}), and the \emph{effect of velocity} in the controller (by performing squares and circles at different velocities, as seen in Section \ref{sec:sect33}).

The new motion controller has a linear drift in the order of $6cm/m$ in the low velocity settings ($2$ to $6cm/s$) and around $9cm/m$ at higher velocities ($6$ to $10cm/s$). The rotational drift is in the order of $2deg/min$ when the robot is moving.

In summary, this project has implemented the high-level functionality needed in order to achieve accurate motion control of the GNBot robots. The self-calibrating nature of the approach also facilitates its use in large robot swarms.
The outcome of the project has been published as open-source in a GitHub repository\footnote{\url{https://github.com/carlosgs/GNBot}}.

\section{Future work}

Using the new controller it will be possible to evaluate search strategies that depend on accurate position-based control (i.e. environment mapping, efficient area covering, flocking behaviours, etc).

In regards to self-calibration, the studied method provides static tuning parameters that remain unchanged until a re-calibration is manually issued.
Some authors have studied SLAM approaches that instead update the calibration estimates automatically in real time\cite{martinelli07,DeCecco02,roy99}.
These techniques could be explored with the incorporation of other forms of odometry such as wheel encoders.

The inertial sensor used in this project includes not only a gyroscope but also an accelerometer. It would be very interesting to incorporate these measurements into the motion controller. For instance, the accelerometer could be used in order to detect changes in ground surface and account for the differences in friction.

% Measure a different brand of servo motors/distance sensor (arduskybot)
% Incorporate the measurements of the accelerometer

\clearpage{\pagestyle{empty}\cleardoublepage}

%% bibliography
\renewcommand{\bibname}{References}
\newpage
\addcontentsline{toc}{chapter}{\bibname}
\bibliographystyle{unsrt}
\bibliography{references}

\end{document}

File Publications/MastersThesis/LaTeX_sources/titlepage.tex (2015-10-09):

% Last modification: 2015-08-17 (Marc Deisenroth)
\begin{titlepage}

\newcommand{\HRule}{\rule{\linewidth}{0.5mm}} % Defines a new command for the horizontal lines, change thickness here

%----------------------------------------------------------------------------------------
%	LOGO SECTION
%----------------------------------------------------------------------------------------

\\[0.5cm] 

\center % Center remainder of the page

%----------------------------------------------------------------------------------------
%	HEADING SECTIONS
%----------------------------------------------------------------------------------------

\textsc{\Large Imperial College London}\\[0.5cm] 
\textsc{\large Department of Computing}\\[0.5cm] 

%----------------------------------------------------------------------------------------
%	TITLE SECTION
%----------------------------------------------------------------------------------------

\HRule \\[0.4cm]
%{ \huge \bfseries \reporttitle}\\ % Title of your document
\begin{spacing}{1.5}
{ \fontsize{0.65cm}{1em} \bfseries \reporttitle}\\ % Title of your document
\end{spacing}
\HRule \\[1.5cm]
 
%----------------------------------------------------------------------------------------
%	AUTHOR SECTION
%----------------------------------------------------------------------------------------

\begin{minipage}{0.4\textwidth}
\begin{flushleft} \large
\emph{Author:}\\
\reportauthor % Your name
\end{flushleft}
\end{minipage}
~
\begin{minipage}{0.4\textwidth}
\begin{flushright} \large
\emph{Supervisor:} \\
\supervisor % Supervisor's Name
\end{flushright}
\end{minipage}\\[4cm]

%----------------------------------------------------------------------------------------
%	FOOTER & DATE SECTION
%----------------------------------------------------------------------------------------
\vfill % Fill the rest of the page with whitespace
Submitted in partial fulfillment of the requirements for the MSc degree in
\degreetype~of Imperial College London\\[0.5cm]

\makeatletter
\@date 
\makeatother

\end{titlepage}

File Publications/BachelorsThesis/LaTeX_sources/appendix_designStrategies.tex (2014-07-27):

\chapter{Publications}
\label{Appendix:designStrategies}
\vspace{-1cm}

This work resulted in the following paper to be presented July 30th at Living Machines 2014\footnote{\url{http://csnetwork.eu/livingmachines/conf2014}} \emph{(3rd International Conference on Biomimetic and Biohybrid Systems)} in Milan, and published in \emph{Springer Lecture Notes in Artificial Intelligence}\footnote{\url{http://link.springer.com/chapter/10.1007\%2F978-3-319-09435-9_10}} series:

\textbf{Carlos García-Saura, Francisco de Borja Rodríguez, and Pablo Varona. Design principles for cooperative robots with uncertainty-aware and resource-wise adaptive behavior. In Armin Duff, Nathan F. Lepora, Anna Mura, Tony J. Prescott, and Paul F.M.J. Verschure, editors, \emph{Biomimetic and Biohybrid Systems}, volume 8608 of \emph{Lecture Notes in Computer Science}, pages 108-117. Springer International Publishing, 2014.}
\cite{GarciaSauraRodriguezVarona14}

A spanish version of the article, entitled ``Dise\~{n}o de una plataforma rob\'{o}tica para la implementaci\'{o}n de algoritmos de b\'{u}squeda cooperativa de fuentes de olor'', has been presented to the \emph{Arquimedes National Research Contest}\footnote{\url{https://sede.educacion.gob.es/catalogo-tramites/becas-ayudas-subvenciones/premios/premios-estudiantes/certamen-arquimedes/certamen-arquimedes-2014.html}}.

\newpage \thispagestyle{empty} % Página vacía

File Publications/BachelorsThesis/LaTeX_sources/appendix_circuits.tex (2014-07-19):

\chapter{GNBoard design schematics and layout}
\label{Appendix:circuits}
\vspace{-1cm}

\begin{figure}[h!]
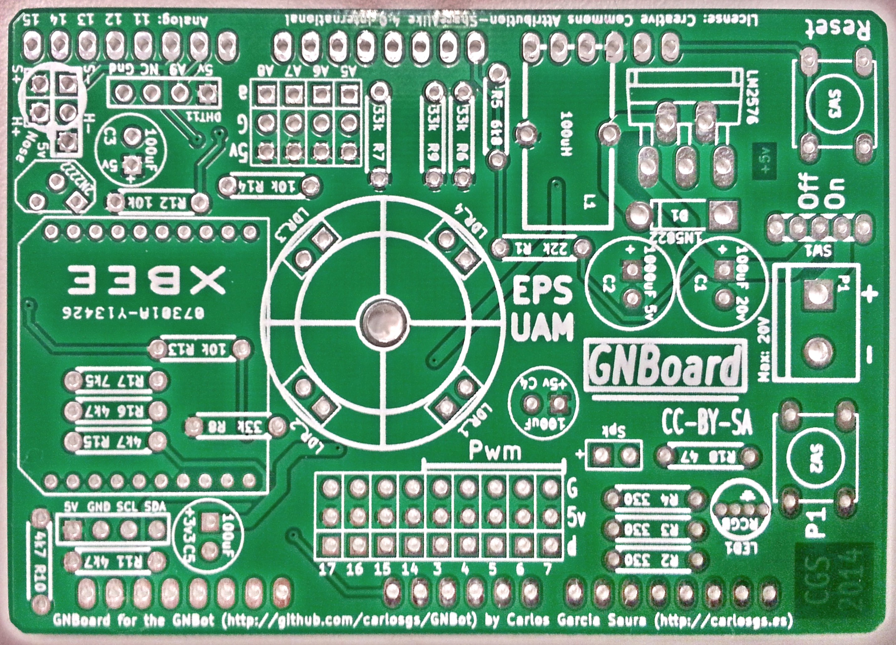
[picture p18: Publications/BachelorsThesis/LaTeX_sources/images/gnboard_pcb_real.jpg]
\centerline{\mbox{}}
\captionFigure{Manufactured PCB for the GNBoard v1.0}
{fig:gnboard_pcb_real}{
A total of 20 boards were ordered to \url{http://www.seeedstudio.com/}. The layout utilizes through-hole components solely, in order to simplify the assembly task.
}
\end{figure}

\newpage
%\thispagestyle{empty}
\begin{figure}[h!]
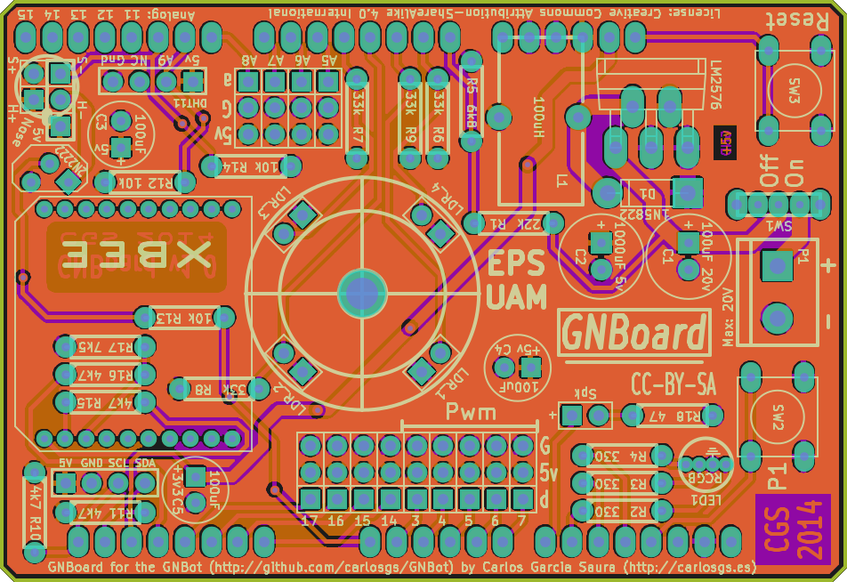
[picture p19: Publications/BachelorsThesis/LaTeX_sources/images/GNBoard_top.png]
\centerline{\mbox{}}
\vspace{0.5cm}
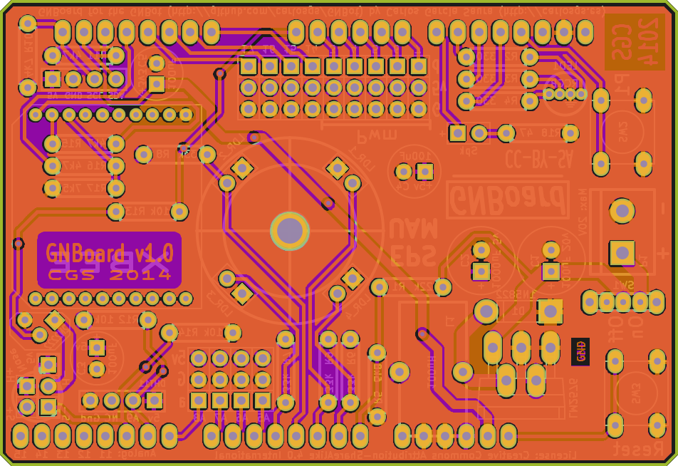
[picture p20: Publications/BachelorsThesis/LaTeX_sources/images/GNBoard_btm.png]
\centerline{\mbox{}}
\centering\captionFigure{GNBoard v1.0 layout}
{fig:GNBoard_layout}{
Top and bottom views.\\
More information can be found in Section \ref{sect:openSourceElectronics}.
}
\end{figure}

\newpage
\thispagestyle{empty}

\newgeometry{top=3.5cm,bottom=4.5cm,left=1cm,right=0cm}

\begin{landscape}

\begin{figure*}[tb] 
\centering
 \makebox[\textwidth]{}
\captionFigure{GNBoard v1.0 schematic}
{fig:GNBoard_schem}{
More information can be found in Section \ref{sect:openSourceElectronics}.
}
\end{figure*}

\end{landscape}

\restoregeometry

\newpage \thispagestyle{empty} % Página vacía

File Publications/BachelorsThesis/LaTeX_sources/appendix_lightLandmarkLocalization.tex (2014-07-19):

\chapter{Robot localization using light landmarks}
\label{Appendix:lightLandmarks}
\vspace{-1cm}

\fancyfoot[CE,CO]{APPENDIX A. LOCALIZATION USING LIGHT LANDMARKS}

This appendix summarizes the work undertaken towards a new system that would allow robot localization in a controlled environment, with the use of low-cost light sensor arrays on board each robot, in combination with purposely placed luminous landmarks.
The scenarios, data generation and techniques used for data processing are explained, and the resulting implementation is evaluated.

\subsection*{Landmark localization approach}

The proposed system would consist in stationary light sources whose position within the monitored area is known.
With a simple sensor array (shown in Fig. \ref{fig:lightLandmarks/LDR_sensor_array}), a robot would then be able to identify the direction and distance of each light source in order to infer its relative position in the environment.
As the utilized sensors were low-cost, the implementation of this technique required the calibration of the light sensor responses and the creation of adaptable models. For instance, the attenuation of light due to distance (Fig. \ref{fig:lightLandmarks/LDR_intensityVSdistance}) was modeled with exponential curve fitting in order to linearize the sensor responses.

\begin{figure}[h!]
\centerline{\mbox{}}
\captionFigure{Low-cost light sensor array for light-based landmark localization}
{fig:lightLandmarks/LDR_sensor_array}{
Light sensor array (left), position diagram (middle) and array mounted in a GNBot (right).
The light sensor array is made of four light-dependent resistors arranged in a ring shape. These are held in position using a 3D-printed shape designed for the purpose, and can be easily connected to the GNBoard electronics. The output is measured as a 10 bit ADC value [0-1023] that is proportional to the resistance.
}\end{figure}

\begin{figure}[h!]
\centerline{\mbox{}}
\captionFigure{Response curve of the light sensors utilized}
{fig:lightLandmarks/LDR_intensityVSdistance}{
The figure shows the measured response of a light sensor at 16 different distances from a light source.
By modeling this response curve it is possible to later infer the distance of a perceived light source.
Details on the employed sensor can be found in Fig. \ref{fig:lightLandmarks/LDR_sensor_array}.
}\end{figure}

\subsubsection{Data generation for light source modeling}

The motion of the robot was restricted to be a rotation over the XY plane to simplify the initial light source modeling experiments. This decision was made since the swarm of robots would be operating in a 2-D environment. By restricting the motion to a rotation, it is possible to evaluate the light intensity measurements more easily. The experiments are described in Figure \ref{fig:lightLandmarks/GNBot_light_landmarks}.

\begin{figure}[h!]
\centerline{\mbox{}}
\captionFigure{GNBot and two light-based landmarks}
{fig:lightLandmarks/GNBot_light_landmarks}{
For the data generation, $N$ light sources were placed in the robot's operating environment. The robot was located on a known spot, where it would make M self-turns spinning at a constant speed while logging the following data:
\vspace{-0.3cm}
\begin{packed_enum}
	\item Intensity of light measured by each sensor of the array
	\item Angle of rotation of the robot measured with the electronic compass
\end{packed_enum}
\vspace{-0.3cm}
At the end, the goal was to determine the direction (angle) and distance to each of the light sources.
}\end{figure}

After some initial tests, a number of measurements were conducted. Each test was repeated both with ambient light and in the dark, with M = 3 full rotations for each experiment.
%\vspace{-0.3cm}
%\begin{packed_enum}
%	\item No light focuses
%	\item One light focus (bright) 
%	\item Two light focuses (both bright) - shown in Fig. \ref{fig:lightLandmarks/GNBot_light_landmarks}
%	\item Three light focuses (two bright, one dim)
%	\item Four light focuses (two bright, two dim)
%\end{packed_enum}
%\vspace{-0.3cm}
One light focus was added at a time, and all the parameters of the experiment (real position of each light, amount of ambient light, and all of the sensor responses) were logged in real time using a Python script.
The measurements did not have any significative noise, so no pre-filtering was required, and Matplotlib was used to represent the data (see Fig. \ref{fig:lightLandmarks/LDR_rawData_experiments}).

\begin{figure}[h!]
\centerline{\mbox{}}
\captionFigure{Data from two different light landmark measurements}
{fig:lightLandmarks/LDR_rawData_experiments}{
\emph{1.A} and \emph{1.B} show the raw data from the two experiments.
\emph{2.A} and \emph{2.B} show the same data with a polar representation.
The actual position of light sources appears as colored circles.
Polar representation was preferred since the temporal dimension did not provide significative information as light sources were time invariant.
}\end{figure}

\subsubsection{Modeling the light-based landmarks}

As the intensity values are recording among an orientation measure (in degrees), the datapoints presented periodicity and thus required special polar treatment (see Fig. \ref{fig:lightLandmarks/LDR_polyfitVSfft}).

%\subsubsubsection{Polar data sampling and smoothing}

\begin{figure}[h!]
\centerline{\mbox{}}
\captionFigure{Smoothing the polar data using FFT low-pass filtering}
{fig:lightLandmarks/LDR_polyfitVSfft}{
The panels show the application of an FFT low-pass filter to smooth light data measurements that are polar. As a first approach, polynomial data curve fitting was used for this task, but the resulted curves presented discontinuities. The periodicity properties of FFT provided continuous results that were more adequate for the task.
}\end{figure}

%\subsubsection{Particle filtering}

%\begin{figure}[h!]
%\centerline{\mbox{\includegraphics[width=15cm]{images/placeholder.eps}}}
%\captionFigure{Diagram showing how the light-landmark localization works}
%{fig:lightLandmarks/}{
%Description
%}\end{figure}

%\subsubsection{Light landmark localization results}

After examining all the resulting data, the selected approach was to use a single light landmark (instead of multiple lights) and to incorporate measurements from both the light sensor array and the electronic compass on board the GNBot.
By measuring its global orientation and the perceived direction to the light source, the robot could then infer its relative position to the landmark (see Fig. \ref{fig:lightLandmarks/LDR_particleFilter_results}).

\begin{figure}[h!]
\centerline{\mbox{}}
\captionFigure{2-D position estimation based on a light landmark}
{fig:lightLandmarks/LDR_particleFilter_results}{
The panels show data from various real robot localization experiments involving a particle filter in combination with measurements from the light sensor array and the electronic compass. Scale is in centimeters. The results have a lot of noise, because of the poor stability of the magnetic field measurement indoors.
}
\end{figure}

The implemented system performed with reasonable accuracy in simulations, but the electronic compass did not perform as expected and made the real world implementation very unreliable (specially when compared with the accuracy of the vision-based tracking system implemented in Section \ref{sect:visionBasedLocalization}).
The problem was that building floors usually have metal structures underneath, so the magnetic field is particularly distorted at low heights. Since the robots are quite low-profile, the magnetometer is then too strongly influenced by the presence of metals in the floor to allow proper robot localization.

Though, this approach for light landmark modeling and localization could be of interest for certain outdoor situations such as underwater positioning, where the light from the Sun does not create much interference.

\newpage \thispagestyle{empty} % Pagina vacia 

\fancyfoot[CE,CO]{\leftmark}

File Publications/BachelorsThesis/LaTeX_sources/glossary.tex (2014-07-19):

\chapter{Glossary}

\begin{itemize}

\item{\textbf{Arduino}: A family of open-source boards generally designed around a single 8-bit Atmel AVR microcontroller. Current models feature a USB interface, analog and digital I/O pins which allows the user to attach various extension boards. (\url{http://www.arduino.cc/})}

\item{\textbf{Arduino shield}: Arduino and Arduino-compatible boards make use of shields - printed circuit expansion boards that plug into the normally supplied Arduino pin-headers.}

\item{\textbf{Ethanol} \emph{(a.k.a. ethyl alcohol or pure alcohol)}: A volatile, flammable, colorless liquid with the structural formula $CH_3CH_2OH$, often abbreviated as $C_2H_5OH$ or $C_2H_6O$. One of its occurrences in nature is as a byproduct of the metabolic process of yeast.}

\item{\textbf{GPS} \emph{(Global Positioning System)}: Space-based satellite navigation system that provides location and time information in all weather conditions, anywhere on or near the Earth where there is an unobstructed line of sight to four or more GPS satellites.}

\item{\textbf{L\'{e}vy walk} \emph{(a.k.a. L\'{e}vy flight)}: A random walk, or path that consists of a succession of random steps, in which the step-lengths have a probability distribution that is heavy-tailed. This means that L\'{e}vy walks combine short steps with longer trajectories, a search behavior that has been observed in many species including sharks, honeybees, and even humans.}

\item{\textbf{Odor Sensor} \emph{(a.k.a. artificial nose, gas sensor)}: Sensing element prominently featured in gas detection equipment in the fields of safety, health, control systems, and instrumentation. Most common odor sensors are based on tin dioxide semiconductor \cite{MillerBakrania06nanostructured}, and one of the leading manufacturers of this kind of technology is Figaro (\url{http://www.figarosensor.com/})}

\item{\textbf{OpenCV} \emph{(Open Source Computer Vision Library)}: An open-source programming library with more than 2500 optimized algorithms, which include a comprehensive set of both classic and state-of-the-art computer vision and machine learning algorithms. (\url{http://opencv.org/})}

\item{\textbf{PCB} \emph{(Printed Circuit Board)}: Structure for mechanically supporting and electrically connecting electronic components with conductive tracks, pads and other features etched from copper sheets laminated onto a non-conductive substrate. PCBs can be single sided (one copper layer), double sided (two copper layers) or multi-layer.}

\item{\textbf{Plume} \emph{(a.k.a. gas plume, odor plume, filamental concentration)}: In hydrodynamics, a plume is a mass of fluid moving through another, and which can be distinguished from the surrounding matter for its different temperature or composition. Plumes evolve in time according to its momentum (inertia), buoyancy (density differences), and diffussion properties.}

\item{\textbf{PrintBots} \emph{(PRINTable roBOTS)}: The family of robots that are open-source and can be manufactured using a low-cost 3D printer. PrintBots are oriented to the community: people in different countries can download and print each of the parts that make a PrintBot, and also modify them and re-share the improvements with the rest of the world. (as defined in \cite{GonzalezValero11miniskybot,ValeroGonzalez12creativity,Garcia-Saura2012,ValeroGonzalezOOML12})}

\item{\textbf{Python}: A widely used general-purpose, high-level programming language that is cross-platform. Its design philosophy emphasizes code readability, and its syntax allows programmers to express concepts in fewer lines of code than what would be possible in languages such as C. (\url{https://www.python.org/})}

\item{\textbf{Servomotor}: Rotatory actuator type that consists of a suitable motor coupled to a sensor for position feedback. Continuous-rotation servomotors do not generally have control over the angular position and can regulate the rotation speed instead. Servomotors are widely used in applications such as robotics, CNC machinery or automated manufacturing.}

\item{\textbf{Transient response} \emph{(a.k.a. natural response)}: The response of a system to a change from equilibrium. The transient response is not necessarily tied to ``on/off'' events but to any event that affects the equilibrium of the system. The \emph{impulse response} and \emph{step response} are transient responses to a specific input (an impulse and a step, respectively).}

\item{\textbf{ZigBee} \emph{(IEEE 802.15.4)}: A specification for a suite of high level communication protocols used to create personal area networks built from small, low-power digital radios. Though low-powered, ZigBee devices can transmit data over long distances by passing data through intermediate devices to reach more distant ones, creating a mesh network. (\url{http://www.zigbee.org/})}

\end{itemize}

\newpage \thispagestyle{empty} % Página vacía

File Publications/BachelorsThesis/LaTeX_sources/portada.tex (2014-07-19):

\begin{titlepage}
%\setcounter{page}{-1}
\setcounter{page}{0}

\begin{center}

\vspace*{-2.2cm}

\LARGE \textbf{\textsc{Universidad Aut\'onoma de Madrid}}\\

\vspace{.2cm}

\Large \textbf{\textsc{Escuela Polit\'ecnica Superior}}\\

\vspace{0.5cm}

\begin{figure}[h]
    \begin{center}
        \begin{minipage}[c]{0.495\linewidth}
            \rightline{\epsfig{figure=images/logo_eps.eps,width=0.5\linewidth}}
        \end{minipage}
        \begin{minipage}[c]{0.495\linewidth}
            \leftline{\epsfig{figure=images/logo_uam.eps,width=0.5\linewidth}}
        \end{minipage}
    \end{center}
    \label{fig:Escudos}
\end{figure}

%\vspace{0.1cm}

\LARGE \textbf{\textsc{Trabajo de fin de grado}}\\
\normalsize \textsc{\textit{BACHELOR'S THESIS}}\\

\vspace{2.5cm}

\large \MakeUppercase{\textbf{Estrategias cooperativas de detecci\'on y localizaci\'on de olores con robots y narices artificiales}}

\large \MakeUppercase{\textit{\titulo}}

\vspace{2.2cm}

\large{Grado en Ingenier\'ia de Tecnolog\'ias y Servicios de Telecomunicaci\'on}\\
\normalsize\textit{\carrera}

\vspace{1cm}

\Large \textbf\autor \\
\vspace{0.5cm}
%\Large Autor: \textbf\autor \\
\large Tutor: \textbf\tutor \\

\vspace{0.5cm}

\LARGE Junio 2014

\end{center}

\end{titlepage}

\normalsize

\newpage \thispagestyle{empty} % Página vacía
\setcounter{page}{0}

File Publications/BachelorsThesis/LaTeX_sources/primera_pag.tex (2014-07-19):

\chapter*{}

\vspace*{-2cm}

\begin{center}

\large \MakeUppercase{\textbf{\titulo}}

\normalsize \MakeUppercase{\textit{Estrategias cooperativas de detecci\'on y localizaci\'on de olores con robots y narices artificiales}}

\vspace{2cm}

\Large Author: \textbf{\autor} \\
\Large Tutor: \textbf{\tutor} \\

\vspace{6cm}

Grupo de Neurocomputaci\'on Biol\'ogica \\
\url{http://www.ii.uam.es/~gnb/} \\
%Dpto. de Ingenier\'ia Inform\'atica \\
\vspace{0.1cm}
Escuela Polit\'ecnica Superior \\
Universidad Aut\'onoma de Madrid \\
\vspace{0.5cm}
\Large \fecha

\end{center}

\normalsize

\newpage \thispagestyle{empty} % Página vacía

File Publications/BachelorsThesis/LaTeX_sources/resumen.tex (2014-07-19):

%\vspace*{-2cm}
\chapter*{Resumen}
\vspace*{-1.5cm}

En este trabajo de investigaci\'{o}n se aborda el dise\~{n}o de una plataforma rob\'{o}tica orientada a la implementaci\'{o}n de estrategias de b\'{u}squeda cooperativa bio-inspiradas. En particular, tanto el proceso de dise\~{n}o de la parte electr\'{o}nica como hardware se han enfocado hacia la validaci\'{o}n en entornos reales de algoritmos capaces de afrontar problemas de b\'{u}squeda con incertidumbre, como lo es la b\'{u}squeda de fuentes de olor que presentan variaci\'{o}n espacial y temporal. Este tipo de problemas pueden ser resueltos de forma m\'{a}s eficiente con el empleo de enjambres con una cantidad razonable de robots, y por tanto la plataforma ha sido desarrollada utilizando componentes de bajo coste.
Esto ha sido posible por la combinaci\'{o}n de elementos estandarizados -como la placa controladora Arduino y otros sensores integrados- con piezas que pueden ser fabricadas mediante una impresora 3D atendiendo a la filosof\'{i}a del hardware libre (open-source).

Entre los requisitos de dise\~{n}o se encuentran adem\'{a}s la eficiencia energ\'{e}tica -para maximizar el tiempo de funcionamiento de los robots-, su capacidad de posicionamiento en el entorno de b\'{u}squeda, y la integraci\'{o}n multisensorial -con la inclusi\'{o}n de una nariz electr\'{o}nica, sensores de luminosidad, distancia, humedad y temperatura, as\'{i} como una br\'{u}jula digital-.
Tambi\'{e}n se aborda el uso de una estrategia de comunicaci\'{o}n adecuada basada en ZigBee.
El sistema desarrollado, denominado GNBot, se ha validado tanto en los aspectos de eficiencia energ\'{e}tica como en sus capacidades combinadas de posicionamiento espacial y de detecci\'{o}n de fuentes de olor basadas en disoluciones de etanol.

La plataforma presentada -formada por el GNBot, su placa electr\'{o}nica GNBoard y la capa de abstracci\'{o}n software realizada en Python- simplificar\'{a} por tanto el proceso de implementaci\'{o}n y evaluaci\'{o}n de diversas estrategias de detecci\'{o}n, b\'{u}squeda y monitorizaci\'{o}n de odorantes, con la estandarizaci\'{o}n de enjambres de robots provistos de narices artificiales y otros sensores multimodales.

\vspace*{-0.2cm}
\section*{Palabras Clave}
\vspace*{-0.2cm}
Plataforma rob\'{o}tica, b\'{u}squeda de olores, robots cooperativos, estrategias de localizaci\'{o}n, nariz electr\'{o}nica, fuentes de olor, rob\'{o}tica de enjambres, bio-inspiraci\'{o}n, vuelos de L\'{e}vy, Python, hardware libre, printbots, impresi\'{o}n 3D, ZigBee, comunicaci\'{o}n a distancia, OpenCV, visi\'{o}n por ordenador, localizaci\'{o}n de robots

%-------------------------------------------------------------
%\begin{center}
%\line(1,0){250}
%\end{center}
%\vspace*{-2cm}
\chapter*{Abstract}
\vspace*{-1cm}

This research work addresses the design of a robotic platform oriented towards the implementation of bio-inspired cooperative search strategies.
In particular, the design processes of both the electronics and hardware have been focused towards the real-world validation of algorithms that are capable of tackling search problems that have uncertainty, such as the search of odor sources that have spatio-temporal variability.
These kind of problems can be solved more efficiently with the use of swarms formed by a considerable amount of robots, and thus the proposed platform makes use of low cost components.
This has been possible with the combination of standardized elements -as the Arduino controller board and other integrated sensors- with custom parts that can be manufactured with a 3D printer attending to the open-source hardware philosophy.

Among the design requirements is the energy efficiency -in order to maximize the working range of the robots-, their positioning capability within the search environment, and multiple sensor integration -with the incorporation of an artificial nose, luminosity, distance, humidity and temperature sensors, as well as an electronic compass-.
Another subject that is tackled is the use of an efficient wireless communication strategy based on ZigBee.
The developed system, named GNBot, has also been validated in the aspects of energy efficiency and for its combined capabilities for autonomous spatial positioning and detection of ethanol-based odor sources.

The presented platform -formed by the GNBot, the GNBoard electronics and the abstraction layer built in Python- will thus simplify the processes of implementation and evaluation of various strategies for the detection, search and monitoring of odorants with conveniently standardized robot swarms provided with artificial noses and other multimodal sensors.

\vspace*{-0.2cm}
\section*{Keywords}
\vspace*{-0.2cm}
Robotic platform, olfactory search, cooperative robots, search strategies, machine olfaction, odor sources, swarm robotics, bio-inspiration, L\'{e}vy walks, Python, open-source hardware, printbots, 3D-printing, ZigBee, remote communications, OpenCV, computer vision, localization of robots

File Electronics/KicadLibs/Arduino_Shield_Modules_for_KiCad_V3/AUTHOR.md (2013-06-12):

Author  
--
Arduino Shield Modules for KiCad V3 by nicholasclewis

License
--
Arduino Shield Modules for KiCad V3 by nicholasclewis is licensed under the Attribution - Creative Commons license (<http://creativecommons.org/licenses/by/3.0/>)

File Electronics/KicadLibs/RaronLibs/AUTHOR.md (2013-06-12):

Author  
--
A few random KiCad components, RGB LED stuff mostly by Raron (<http://raronoff.wordpress.com/2010/08/08/a-few-random-kicad-components-rgb-led-stuff-mostly/>)  

License  
--
This work is licensed under a Creative Commons Attribution-ShareAlike 3.0 Unported License (<http://creativecommons.org/licenses/by-sa/3.0/>)

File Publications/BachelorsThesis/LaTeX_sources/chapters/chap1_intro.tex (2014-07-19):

\chapter{Introduction}
\label{chap:intro}
\vspace{-1cm}

\lsection{Motivation. The problem of odor localization}

The use of new technologies based on artificial noses for the detection and classification of odor sources has the potential to be a true game-changer in many fields \cite{stitzel2011artificial, wilson2009applications}. Tasks such as security monitoring for the detection of high-risk substances/gases in residential and industrial environments, food quality control assessment \cite{DymerskiChmiel11}, environmental protection and field measurement, biometric identification \cite{RodriguezLujan2013279}, medical control \cite{YanezToledano12}, noninvasive routine monitoring, etc, are all taking benefit from the improvements of these techniques.
Moreover, the combination of modern machine olfaction technologies with mobile robotics allows to implement new target identification algorithms that can tackle not only detection tasks \cite{vazquez2013integracion} but higher level odor-related search and monitoring tasks as well \cite{Hu2013, Marjovi2011, marjovi2010olfactory, song2011olfaction, jatmiko2011robots, Marques2006, Hayes02distributedodor}.

While simulated environments are often successfully used to demonstrate the performance of generic search tasks \cite{Mcgill2011,HayesMG01}, the chaotic nature of gases and odor plumes often create a poor balance between the accuracy and computational requirements of the models \cite{Torney2009}.
Most odorants have latency and decay, which turn out to be complex temporal structures that are difficult to model.
This is why it is so important to step out of simulations and have a way to actually test odor search algorithms in the real world \cite{Hu2013, Marjovi2013, song2011olfaction, HayesMG03}.
Also, the uncertainty inherent to the problem of odor localization seems to make possible a drastic reduction in the completion time by parallelizing the search with more than a single agent \cite{Hu2013, Marjovi2013, Marjovi2011, Hayes02distributedodor, HayesMG01}. Here is where the cooperation among robots comes into play, as it is possible to implement a wide range of collaborative search algorithms that include centralized, de-centralized and distributed approaches \cite{Hu2013, Mcgill2011, marjovi2010olfactory}.

Thus, the main motivation and goal of this work is to provide the scientific community with an open robotic platform that simplifies the process of implementing and testing such kind of odor search algorithms.
The developed robots will incorporate artificial noses by design, and the high-level control system will allow to use them efficiently as a active odor-sensing networks.
Novel bio-inspiration for collaborative strategies could finally provide efficient solutions to odor search tasks \cite{Mcgill2011, Reynolds2013, Dunbabin2012, raey10, KongcunM09, arleo07}, and these types of platforms are needed in order to accelerate their incorporation and fulfillment of necessities in industry and in other aspects of the society.

\lsection{State of the art. Odor detection and robotics}

This project has its base in previous work developed at \emph{Grupo de Neurocomputaci\'{o}n Biol\'{o}gica} in \emph{Universidad Aut\'{o}noma de Madrid}. An electronic nose module called ``Olus2'' (Fig. \ref{fig:introduction/OlusAndTGS2600}), created by David Y\'{a}\~{n}ez from Deutecno\footnote{\url{http://www.deutecno.com/}}, has already been used to evaluate various odor detection and classification tasks \cite{YanezToledano12, Yanez09}.
The Olus2 module has also been integrated with a modular robot in a project by Tom\'{a}s V\'{a}zquez Rubio \cite{vazquez2013integracion}, to demonstrate response upon odor perception of a snake-shaped robot. Also, the ongoing work at the group by Alejandro Peque\~{n}o Zurro -who is currently addressing the single-robot odor localization task- has provided to be an enriching collaboration towards a better characterization the odor sensor response.

%Tin odor sensors. How do they work?
The sensing element of most artificial noses is usually a semiconductor based on \emph{tin dioxide} ($SnO_2$).
With the adequate manufacturing technique it is possible to create tin dioxide based materials that present conductivity variations in the presence of a gas.
Those variations in conductivity are measured to be proportional to the perceived concentrations of gas, so the sensor can be effectively modeled as a resistor that varies with odor intensity. Though, the transient responses of tin oxide sensors are usually very pronounced and can make the concentration-measurement task non-trivial.
Also, the semiconductor material needs to be heated up in order to have odor sensitivity, so these kind of sensors usually include a resistive heating element.
Tin dioxide gas sensors are often used in breath analyzers and smoke alarms due to their good sensitivity to organic compounds like ethanol and carbon monoxide \cite{wilson2009applications, stitzel2011artificial}.
A strongly recommended lecture to understand the underlying principles and inner working of these types of sensors is ``Nanostructured Tin Dioxide Materials for Gas Sensor Applications'' by T.A. Miller et al. \cite{MillerBakrania06nanostructured}.

\begin{figure}[h!]
\centerline{\mbox{}}
\captionFigure{Olus2 artificial nose module and odor sensor detail}
{fig:introduction/OlusAndTGS2600}{
Olus2 modules (left) incorporate the TGS2600 odor sensor (right), which is based on tin dioxide semiconductor. Sources: \cite{vazquez2013integracion} and \url{http://figaro.com/}}
\end{figure}

%Odor source modeling
Whilst gas-sensor technology has becomed quite advanced in the last years \cite{pearce2003handbook}, there is still no ideal solution to be found, and the detection of odors has to rely on quite uncertain and noisy responses.
Even with a noisy sensory input, the odor search problem would be trivial to solve if odor concentrations were gradients that varied monotonically according to distance - but that is not the case. The random nature of odor plumes adds up into the equation and the complexity of the problem increases dramatically \cite{Torney2009}.
There is also variability in the types of odor sources that can be used as targets. As the molecular structure of scent particles provides each odorant with different fading times, it is not only needed to model the effective detection area of the odor plume but also its latency and evolution over time \cite{Mcgill2011}.

%Multimodal sensor integration
Having a good model of the target is then a crucial part towards the localization of odors, but those models must account for the uncertainty in the odor sensor response. These imprecisions, inherent to gas sensing, can be tackled with the particularly interesting approach that is multimodal sensor integration \cite{Hein24072012, song2011olfaction, arleo07}. The incorporation of other types of input from devices like video cameras, proximity sensors or air flow directivity sensors, can contribute to remove noise and increase the precision of odor plume detections \cite{Marjovi2013, Hayes02distributedodor}.
In the cases where the odor sources are not disperse but very localized instead, it can be possible to use a simple threshold model and obtain reasonable results \cite{vazquez2013integracion, acosta2013diseno}.

The other critical factor towards an efficient solution to the odor search task is the selection of a sensible search strategy. Search algorithms have been extensively studied for many decades, and the most popular approaches can be classified in three main groups: gradient-based algorithms (i.e. hill climbing \cite{Mcgill2011}), probabilistic methods (i.e. environment mapping \cite{FoxKo05}, bayesian, kalman or particle filters \cite{jatmiko2011robots}), and biologically inspired algorithms (i.e. biased random walks \cite{Hein24072012} or chaotic search \cite{KongcunM09}).
Gradient-based algorithms can be susceptible to local maxima and they depend on the monotonic variation of measurements, which as has been discussed is not the case for odor plumes. Probabilistic search methods and mapping, while requiring high computational resources and memory, are often the preferred approach when the environment is fully characterized.
Bio-inspired search algorithms, on the other hand, come into play when there is uncertainty within the definition of a search problem (i.e. when the search area is not well defined or odor sources may appear and disappear with different latencies).
All of these algorithms can be applied to single-agent tasks and to multi-robot search as well.

%\cite{Mcgill2011} % REVIEW General solutions to search of multiple emission sources
% The lack of a common set of validation cases and reference algorithms that form a ground truth for comparative analysis makes it impossible to directly compare the different algorithms and weigh their merits for different applications. This begs the questions of what should such a reference set involve and how should comparative analysis be performed. Some obvious characteristics are clearly relevant from the literature and evident in Table I: the initial distribution of sources and robots, the presence of obstacles, background ﬂow, dead space (involving no perceptible gradient) and occluded sources, the level of disparity between source strengths, and the time-varying nature of source injection and removal.
% Gradient-based algorithms (i.e. hill climbing), which can be susceptible to local maxima.
% Probabilistic methods (i.e. mapping and bayesian, Kalman or particle ﬁltering), which usually require high computational power
% Biologically inspired algorithms: biased random walks

%\cite{FoxKo05} % A Hierarchical Bayesian Approach to the Revisiting Problem in Mobile Robot Map Building

\subsection{Cooperative search strategies}

\vspace{-0.3cm}
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

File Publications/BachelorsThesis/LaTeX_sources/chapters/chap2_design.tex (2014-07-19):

\chapter{Design and development of the GNBot odor-sensing robotic platform}
\label{chap:design}
\vspace{-1cm}

For the robot design, existing open-source projects were used as a base. The preferred designs had most mechanical parts intended to be manufactured with a low-cost 3D printer. These are called \emph{printbots} \cite{GonzalezValero11miniskybot, ValeroGonzalez12creativity, ValeroGonzalezOOML12}, and one example is the
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

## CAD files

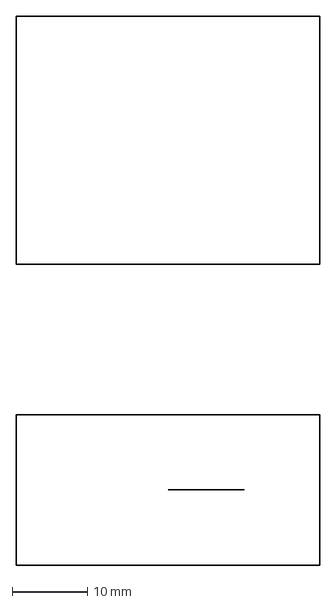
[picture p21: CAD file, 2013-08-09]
Hardware/GNBot_scad_v2.4/src/futaba3003/futaba-main.dxf
40.3 x 73.0 mm

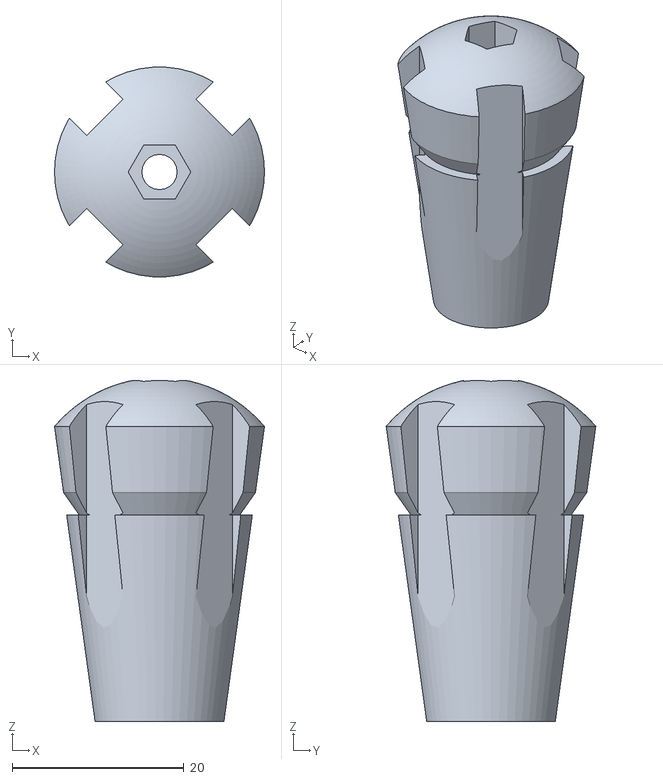
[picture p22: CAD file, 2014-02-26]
Hardware/Attachments/LDR_support/LDR_sensor_array_support.stl
24.4 x 24.4 x 39.7

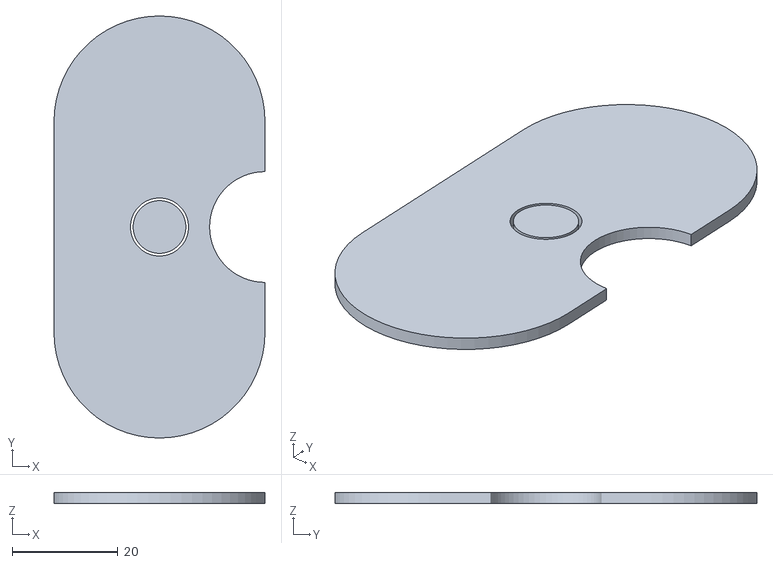
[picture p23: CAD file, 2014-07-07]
Hardware/Attachments/VisualMarkers/STL/tag.stl
40.0 x 80.0 x 2.00

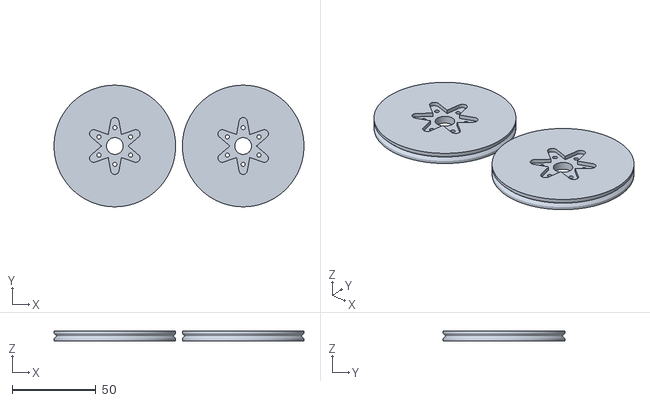
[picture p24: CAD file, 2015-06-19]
Hardware/GNBot_scad_v2.4/Servo-wheel_large.stl
149.0 x 72.5 x 6.00

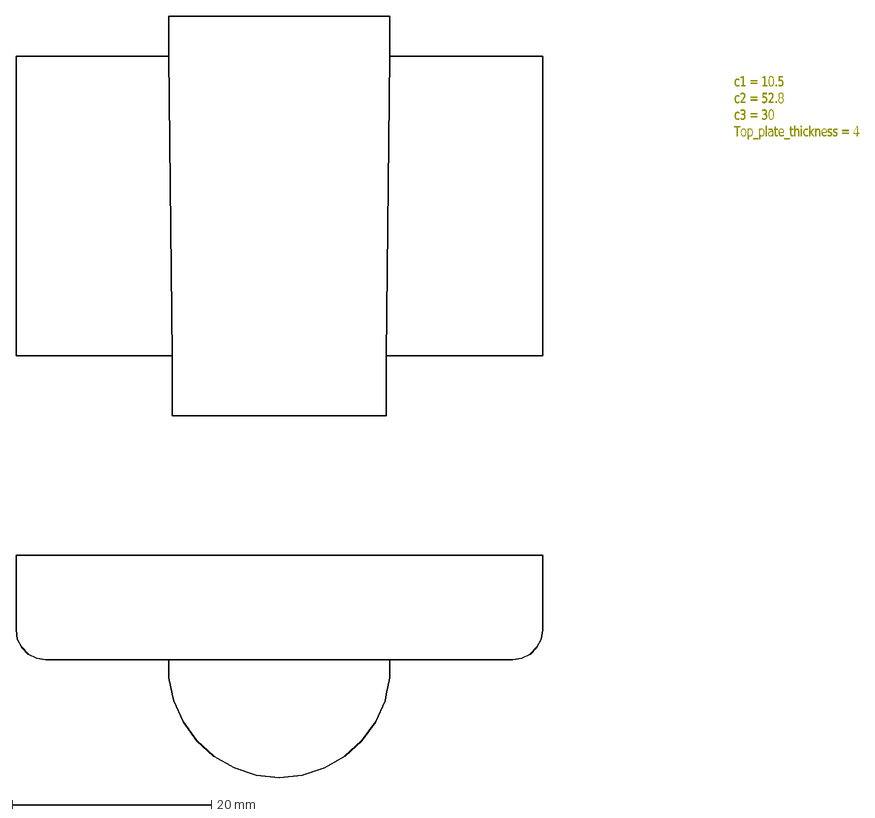
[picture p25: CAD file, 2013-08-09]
Hardware/GNBot_scad_v2.4/src/doc/rear_doc.dxf
c1 = 10.5 c2 = 52.8 c3 = 30 Top_plate_thickness = 4

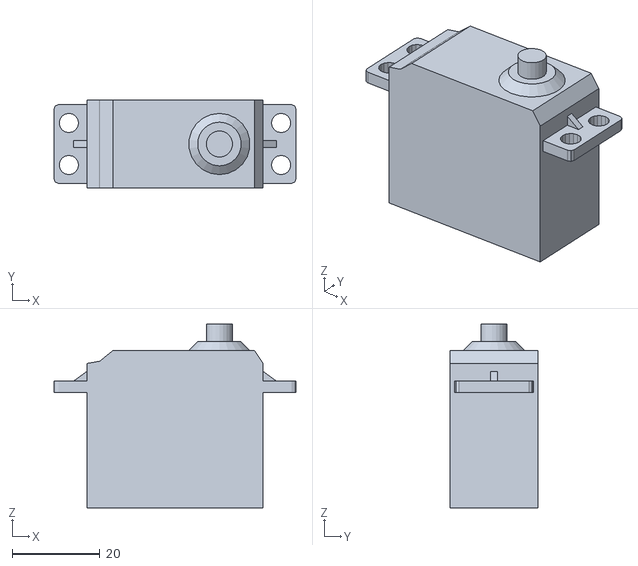
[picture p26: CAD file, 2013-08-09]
Hardware/GNBot_scad_v2.4/src/futaba3003/futaba.stl
55.3 x 20.0 x 42.0

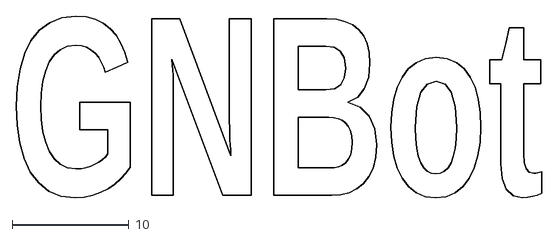
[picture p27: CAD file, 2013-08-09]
Hardware/GNBot_scad_v2.4/src/Text_GNBot.dxf
45.0 x 15.6

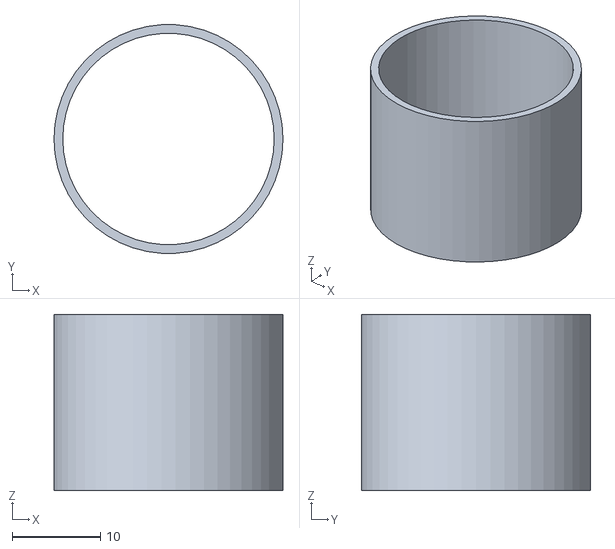
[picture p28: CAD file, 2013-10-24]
Hardware/LDR_support/LDR_sensor_array_support_cover.stl
26.0 x 25.9 x 20.0

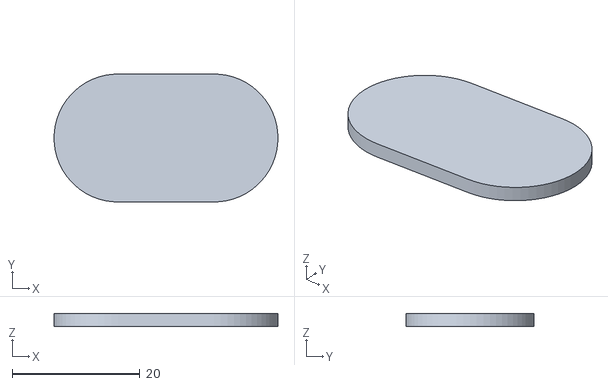
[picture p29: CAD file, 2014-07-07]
Hardware/Attachments/VisualMarkers/STL/angleTag.stl
35.0 x 20.0 x 2.00

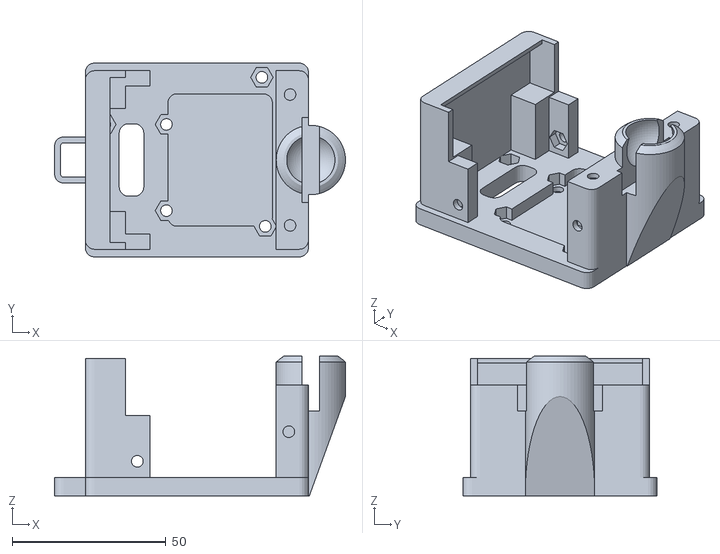
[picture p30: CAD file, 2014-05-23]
Hardware/GNBot_scad_v2.4/GNBot_chassis_v2.4.stl
94.5 x 63.0 x 45.3

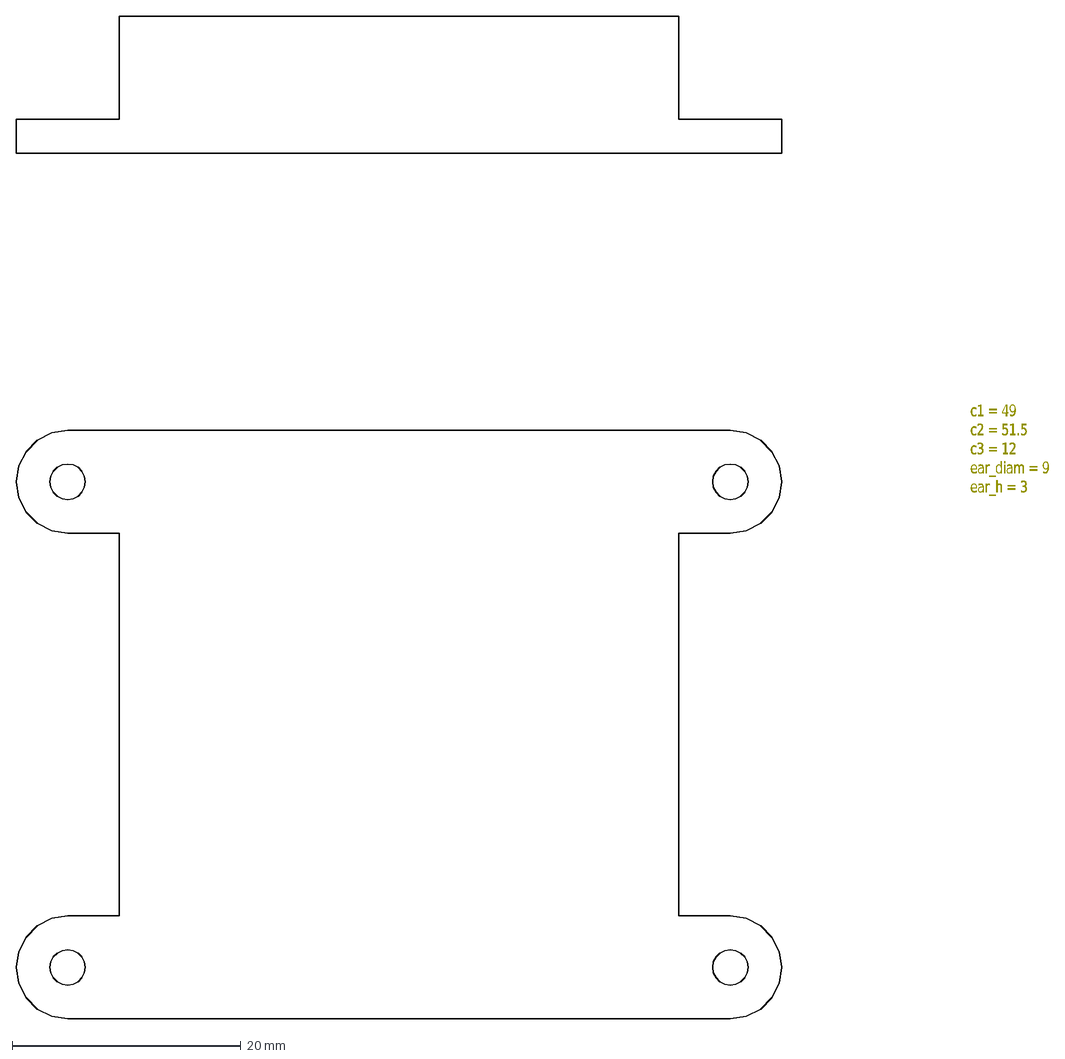
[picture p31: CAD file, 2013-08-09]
Hardware/GNBot_scad_v2.4/src/doc/battery_holder.dxf
c1 = 49 c2 = 51.5 c3 = 12 ear_diam = 9 ear_h = 3

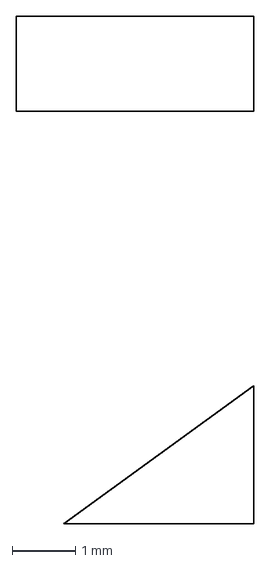
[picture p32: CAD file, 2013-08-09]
Hardware/GNBot_scad_v2.4/src/futaba3003/futaba-ears2.dxf
3.75 x 8.00 mm

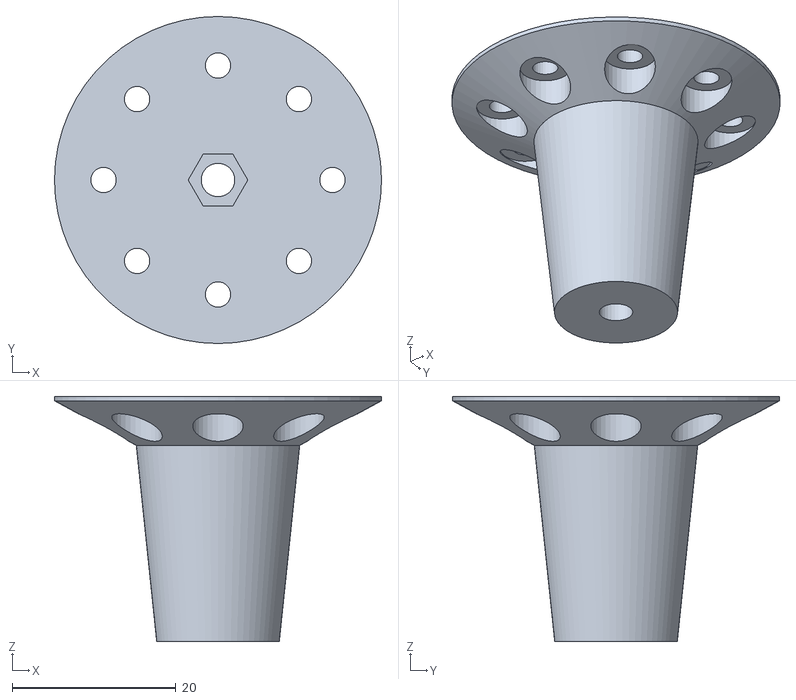
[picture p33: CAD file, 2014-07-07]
Hardware/Attachments/VisualMarkers/STL/target_support.stl
40.0 x 40.0 x 30.0

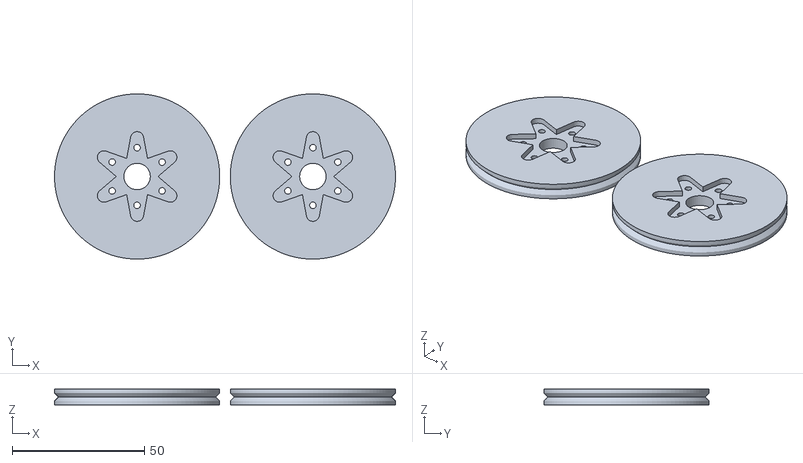
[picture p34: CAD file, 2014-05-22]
Hardware/GNBot_scad_v2.4/Servo-wheel.stl
129.0 x 62.5 x 6.00

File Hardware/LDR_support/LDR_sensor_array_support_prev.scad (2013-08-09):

// This file is part of GNBot (https://github.com/carlosgs/GNBot)
// by Carlosgs (http://carlosgs.es)
// CC-BY-SA license (http://creativecommons.org/licenses/by-sa/3.0/)

drill_resolution = 40;
drill_diameter = 3.5;

LDR_width = 6;
LDR_height = 5;

piece_height = 12;

intersection() {
    difference() {

        //cylinder(r=25/2,h=piece_height,$fn=50);
        translate([0,0,piece_height/2])
          roundedRect2D([25,25,piece_height], 9);

        //cylinder(r=8/2,h=200,center=true,$fn=drill_resolution);
        cube([LDR_width,LDR_width,100],center=true);

        for (i = [0:2])
          rotate([0,0,i*360/3+90]) translate([8,0,0])
	        cylinder(r=drill_diameter/2,h=10,center=true,$fn=drill_resolution);

        translate([0,0,piece_height])
          cube([13.5,13.5,4*2],center=true);

        translate([0,0,2+LDR_height/2]) {
            cube([LDR_width,100,LDR_height],center=true);
            cube([100,LDR_width,LDR_height],center=true);
        }


    }

    sphere(r=15,$fn=50);

}//intersection


// http://www.thingiverse.com/thing:9347
module roundedRect2D(size, radius)
{
    $fn=50;
    x = size[0]-radius*2;
    y = size[1]-radius*2;
    z = size[2];

    minkowski()
    {
        cube(size=[x,y,z],center=true);
        cylinder(r=radius,h=0.00001);
    }
}

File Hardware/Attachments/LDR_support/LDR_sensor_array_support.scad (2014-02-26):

// This file is part of GNBot (https://github.com/carlosgs/GNBot)
// by Carlosgs (http://carlosgs.es)
// CC-BY-SA license (http://creativecommons.org/licenses/by-sa/3.0/)

LDR_angle = 45;

LDR_count = 4;

LDR_radius = 18/2;

cyl_btm_r = 15/2;

drill_resolution = 40;
drill_diameter = 3.5;

LDR_width = 6;
LDR_height = 5;
LDR_depth = 4;

piece_height = 40;
top_radius = 16;

cover_thickness = 1;
cover_margin = 1;
cover_height = piece_height-5;

screw_support_thickness = 3;
nut_d = 7.3; // M3
screw_d = 4.1; // M3

ring_h = 24;
ring_thick = 1.4;

// Linear interpolation to fit the ring to the cone shape
ring_r = 0.5+(1-ring_h/piece_height)*cyl_btm_r+(ring_h/piece_height)*(LDR_radius+LDR_depth);

module LDR_sensor_array_support() {
    intersection() {
        difference() {
            cylinder(r1=cyl_btm_r,r2=LDR_radius+LDR_depth,h=piece_height,$fn=50);
            translate([0,0,screw_support_thickness]) // nut slot
                cylinder(r=nut_d/2,h=100,$fn=6,center=false);
            cylinder(r=screw_d/2,h=100,$fn=20,center=true); // screw drill

            for (i = [0:LDR_count-1])
              rotate([0,0,i*360/LDR_count+LDR_angle]) translate([LDR_radius+LDR_depth/2,0,piece_height/2])
                cube([LDR_depth,LDR_width,2*piece_height],center=true);

            translate([0, 0, ring_h])
                rotate_extrude($fn = 50)
                    translate([ring_r, 0, 0])
                        rotate([0,0,45])
                            polygon([[-ring_thick,ring_thick],[2,2],[0,0]]);
                            //square([ring_thick,ring_thick]);
        }

        union() {
            cylinder(r=top_radius,h=piece_height-top_radius,$fn=50);
            translate([0,0,piece_height-top_radius]) sphere(r=top_radius,$fn=100);
        }

    }//intersection
}

LDR_sensor_array_support();

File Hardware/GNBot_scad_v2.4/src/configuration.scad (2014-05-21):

//------------------------------------
//-- Miniskybot 2 configuration file
//------------------------------------

//-- drills
drill_M3 = 3.8;

//-- captive Nuts
nut_h = 3.4;
nut_radius = 7.3/2;

//------------------------------------------------
//-- Servo parameters
//-- See the doc/futaba-doc2.dxf file
//------------------------------------------------
//-- Servo futaba 3003 dimensions
servo_c1 = 20;
servo_c2 = 7.5;
servo_c3 = 29;//CGS MOD
servo_c4 = 41;  // CGS MOD
servo_c5 = 30.3;
servo_c6 = 10;
servo_c7 = 11.6;
servo_c8 = 4.1;
servo_c9 = 5.2;
servo_c10 = 9.6;

//-------------------------------------------
//-- Battery holder parameters
//-- See the doc/battery_holder.dxf file
//-------------------------------------------
battery_c1 = 49;
battery_holder_front_width = 53.5;
battery_c2 = 51.5;
battery_holder_front_gap = 8+0.5;
battery_holder_front_thickness = 0.35*4;
battery_c3 = 12+battery_holder_front_gap;
battery_ear_diam = 9;
battery_ear_h = 3;
battery_top_gap = 1;  
//-- Real battery height whith batteries inserted
battery_height = battery_c3 + battery_top_gap;

//----------------------------------
//-- Rear part parameters
//-- See the doc/rear-doc.dxf file
//----------------------------------
rear_c1 = servo_c2 + 3;
rear_c2 = servo_c3*2;
rear_c3 = servo_c1 + battery_height -battery_ear_h;
rear_edge_rad = 3;

//-- Ball caster parameters
WallThickness = 2.25; //thickness of the retaining wall
BallSize = 16.2+0.5;  //diameter of  your ball bearing.
Airgap = .65;  // Gap between ball and wall  
BallProtrude = .43; //percentage of ball radius sticking out 
WheelDiameter = 56;  //what size wheels you will use.

//-- Wheels parameters
wheels_diam = 56;
wheel_height = 6;
wheel_gap = 1;

//-- ultrasounds
ultrasound_hole = 16.5;
ultrasound_base_lx = 24+1;
ultrasound_base_ly = 20+1;
ultrasound_base_lz = 3;
ultrasound_length = 12.5;
ultrasound_drill_1 = [-9,7,0];
ultrasound_drill_2 = [9,-8,0];

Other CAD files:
Hardware/GNBot_scad_v2.4/src/doc/futaba-doc2.dxf
Hardware/GNBot_scad_v2.4/src/futaba3003/futaba-plate.dxf
Hardware/GNBot_scad_v2.4/battery_holder.stl
Hardware/GNBot_scad_v2.4/src/futaba3003/futaba-ears.dxf
Hardware/GNBot_scad_v2.4/src/main.scad
Hardware/Attachments/LDR_support/previous/LDR_sensor_array_support.scad
Hardware/Attachments/LDR_support/previous/LDR_sensor_array_support.stl
Hardware/Attachments/VisualMarkers/STL/old_tag.stl
Hardware/Attachments/VisualMarkers/tag.scad
Hardware/Attachments/VisualMarkers/target_support.scad
Hardware/GNBot_scad_v2.4/src/Parameterized_battery_holder.scad
Hardware/GNBot_scad_v2.4/src/Servo-wheel.scad
Hardware/GNBot_scad_v2.4/src/battery_holder.scad
Hardware/GNBot_scad_v2.4/src/fake_ultrasound.scad
Hardware/GNBot_scad_v2.4/src/functions.scad
Hardware/GNBot_scad_v2.4/src/futaba3003/Futaba-shaft.dxf
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

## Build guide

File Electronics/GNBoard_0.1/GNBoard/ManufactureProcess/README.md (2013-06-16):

Manufacture process for the GNBoard v0.1  
============

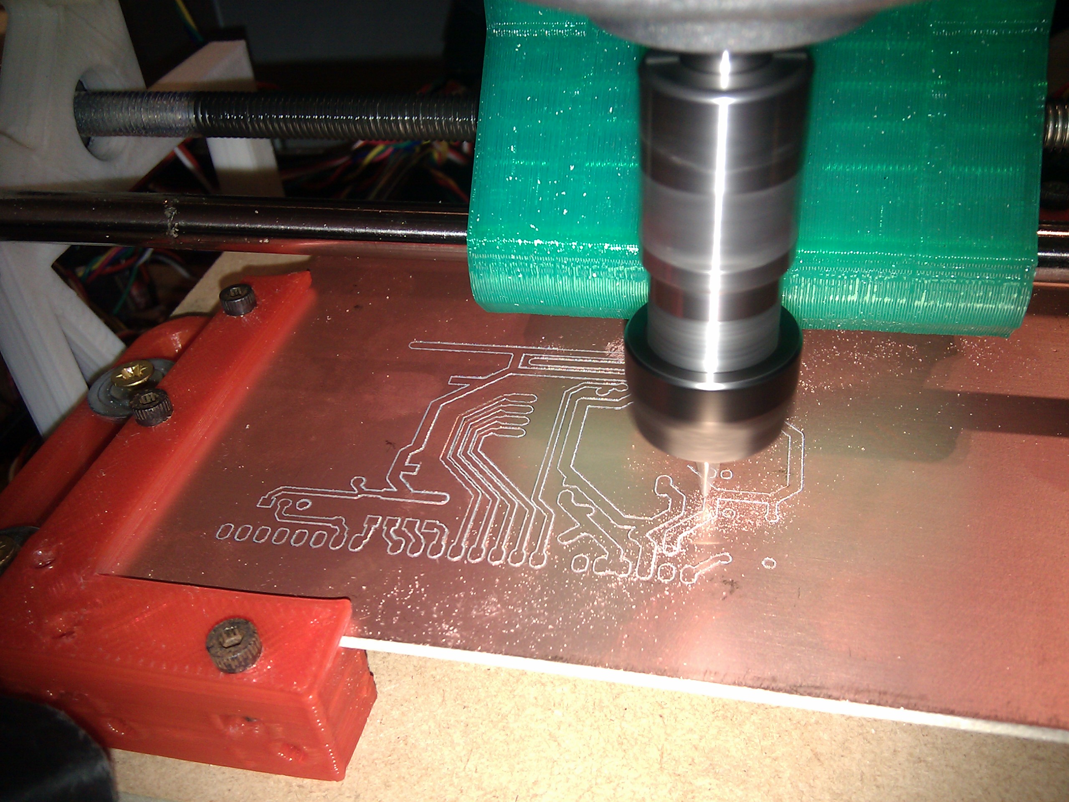
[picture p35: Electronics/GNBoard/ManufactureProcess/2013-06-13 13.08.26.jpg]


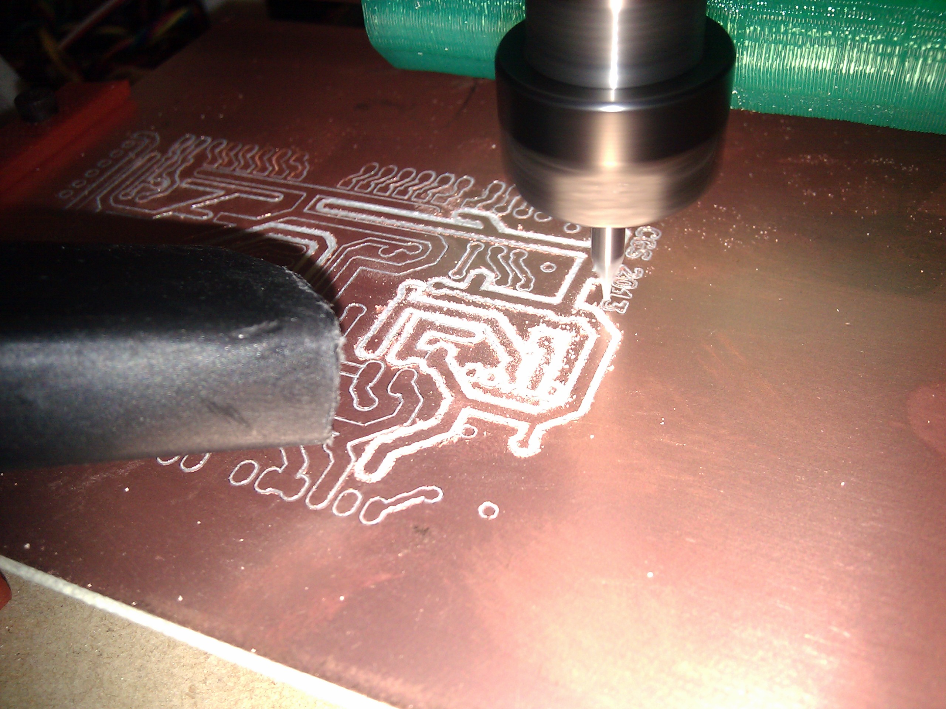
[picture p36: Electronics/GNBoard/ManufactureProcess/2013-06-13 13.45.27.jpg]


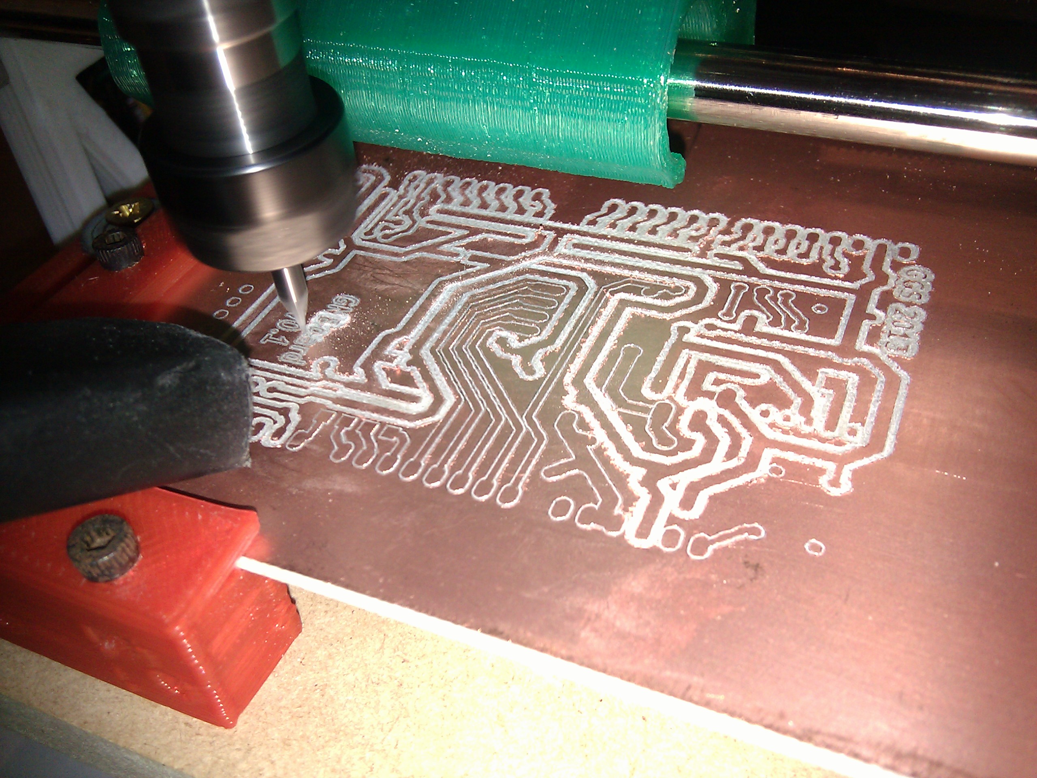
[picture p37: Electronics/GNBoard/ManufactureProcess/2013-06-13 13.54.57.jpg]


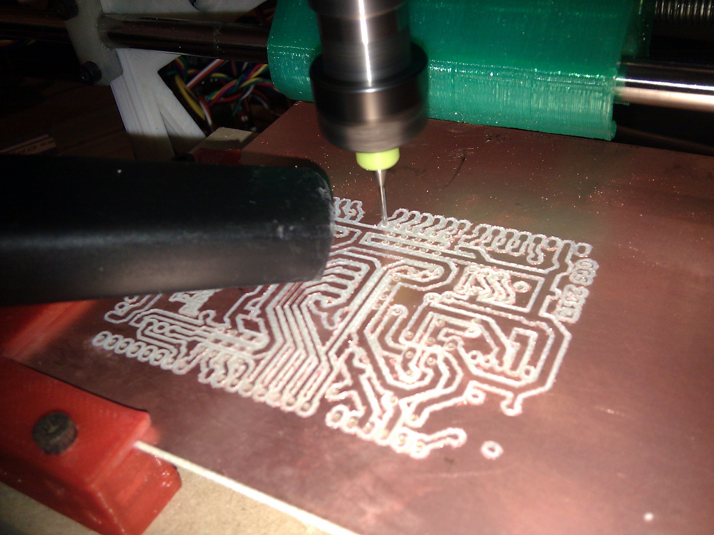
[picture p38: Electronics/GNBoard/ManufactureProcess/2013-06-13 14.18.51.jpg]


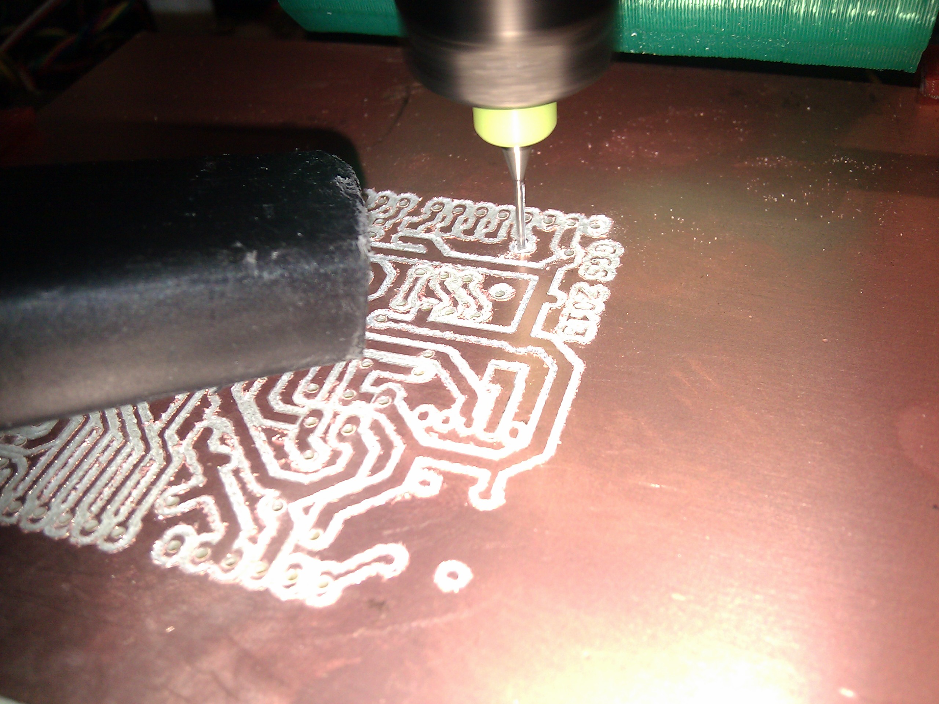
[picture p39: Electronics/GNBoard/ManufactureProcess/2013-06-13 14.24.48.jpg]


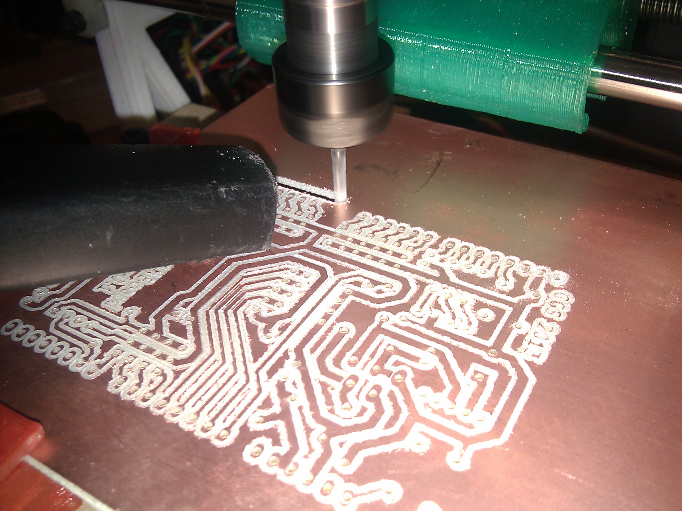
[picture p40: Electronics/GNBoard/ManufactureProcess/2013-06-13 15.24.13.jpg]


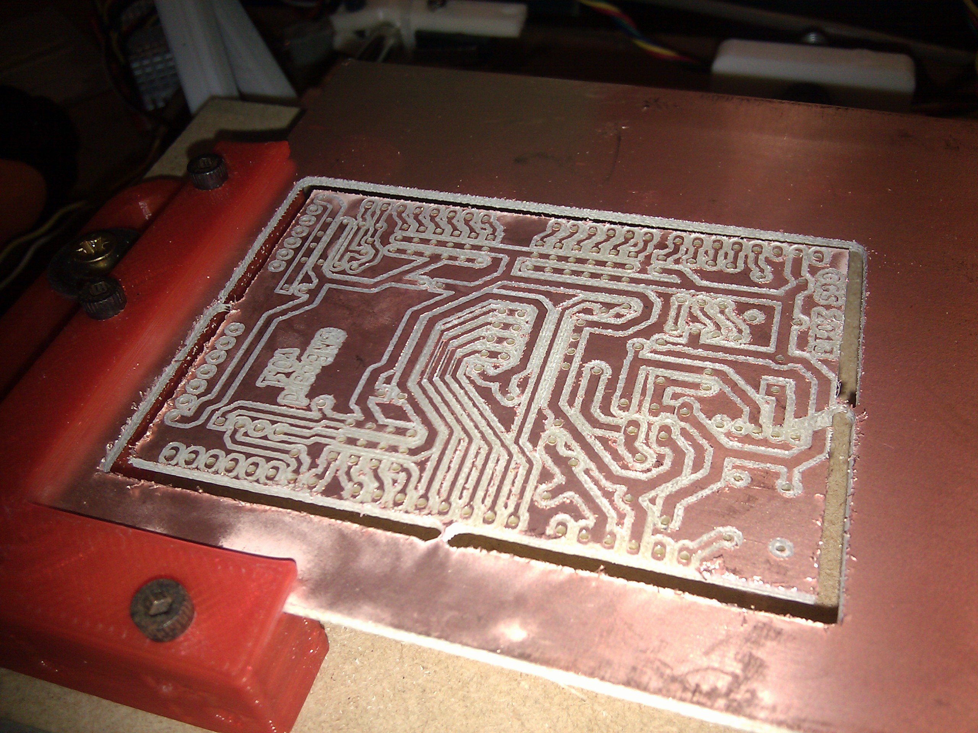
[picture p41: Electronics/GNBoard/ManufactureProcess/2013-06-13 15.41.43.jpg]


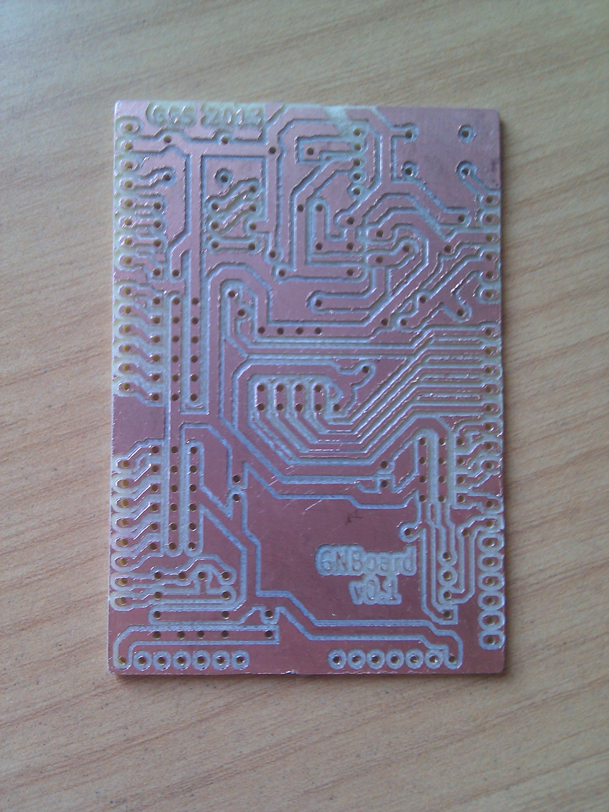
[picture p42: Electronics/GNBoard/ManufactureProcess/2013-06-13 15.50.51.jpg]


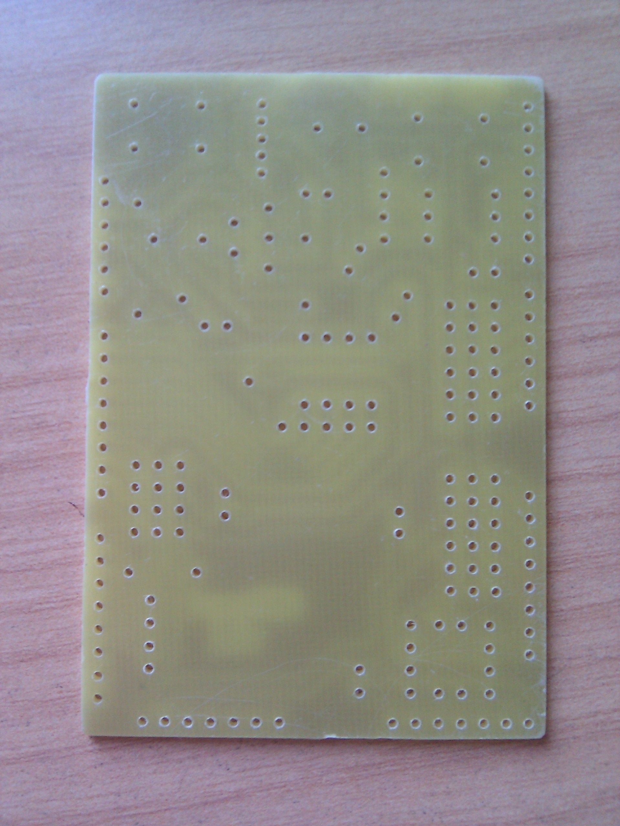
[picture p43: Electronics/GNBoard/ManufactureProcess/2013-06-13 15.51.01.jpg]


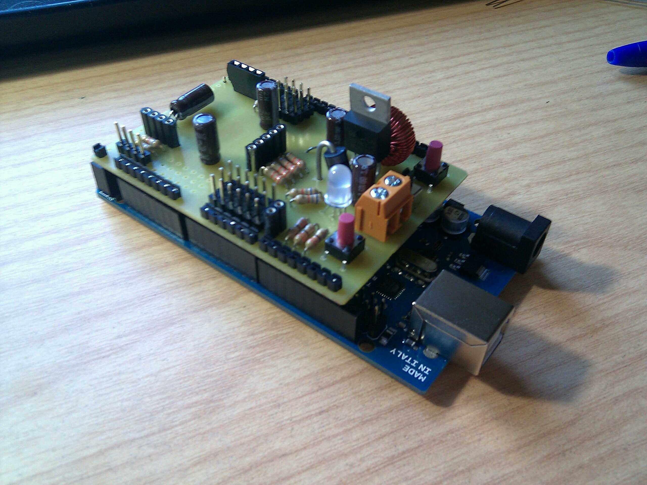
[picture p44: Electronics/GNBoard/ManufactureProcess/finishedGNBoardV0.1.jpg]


Here you can see in detail a pad that was cut due to a bug in the software. _The big decoupling capacitor was a previous try to fix the problem_
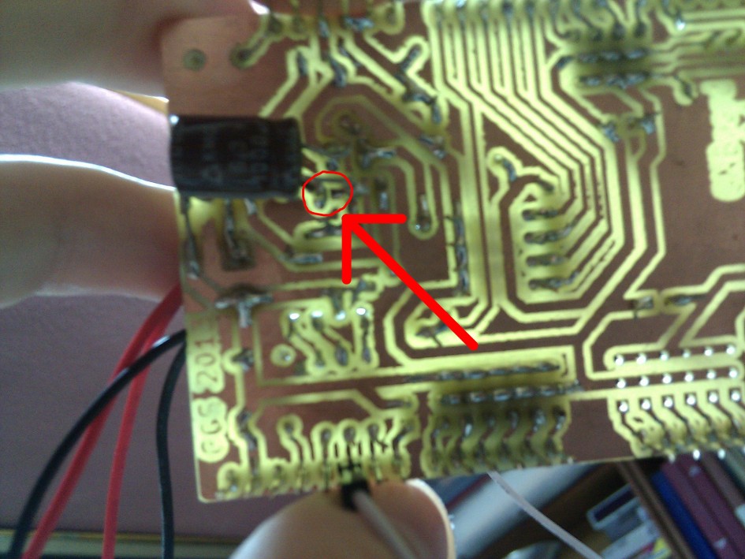
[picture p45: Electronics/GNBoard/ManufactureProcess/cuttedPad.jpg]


License  
--
License: **Attribution - Share Alike - Creative Commons (<http://creativecommons.org/licenses/by-sa/3.0/>)**  

Author:  
--
- **Carlosgs (<http://carlosgs.es>)**

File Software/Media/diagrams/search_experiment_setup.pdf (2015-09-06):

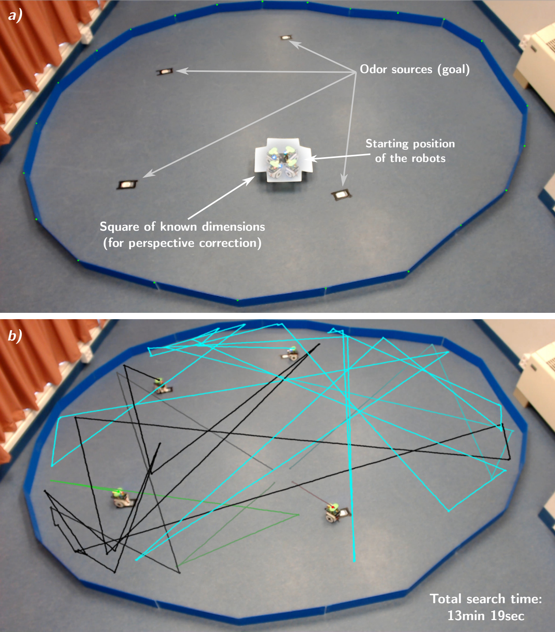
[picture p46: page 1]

b)

a)

Odor sources (goal)

Square of known dimensions (for perspective correction)

Starting position
of the robots

Total search time:
13min 19sec

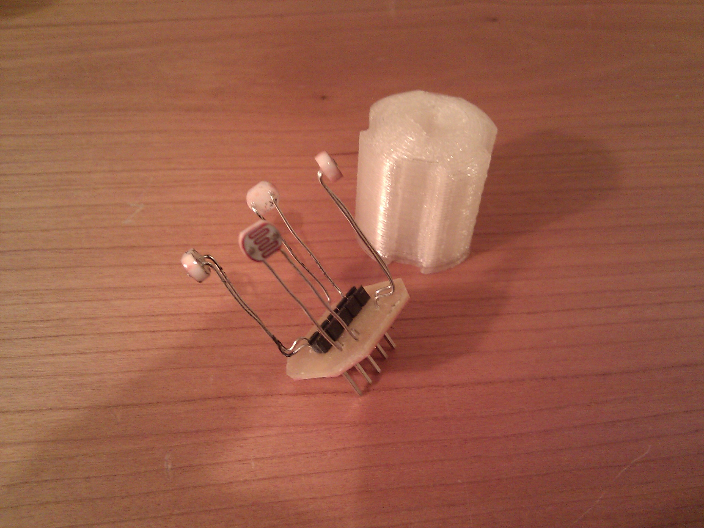
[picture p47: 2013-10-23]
Publications/Media/Robot assembly/2013-08-08 20.51.54.jpg

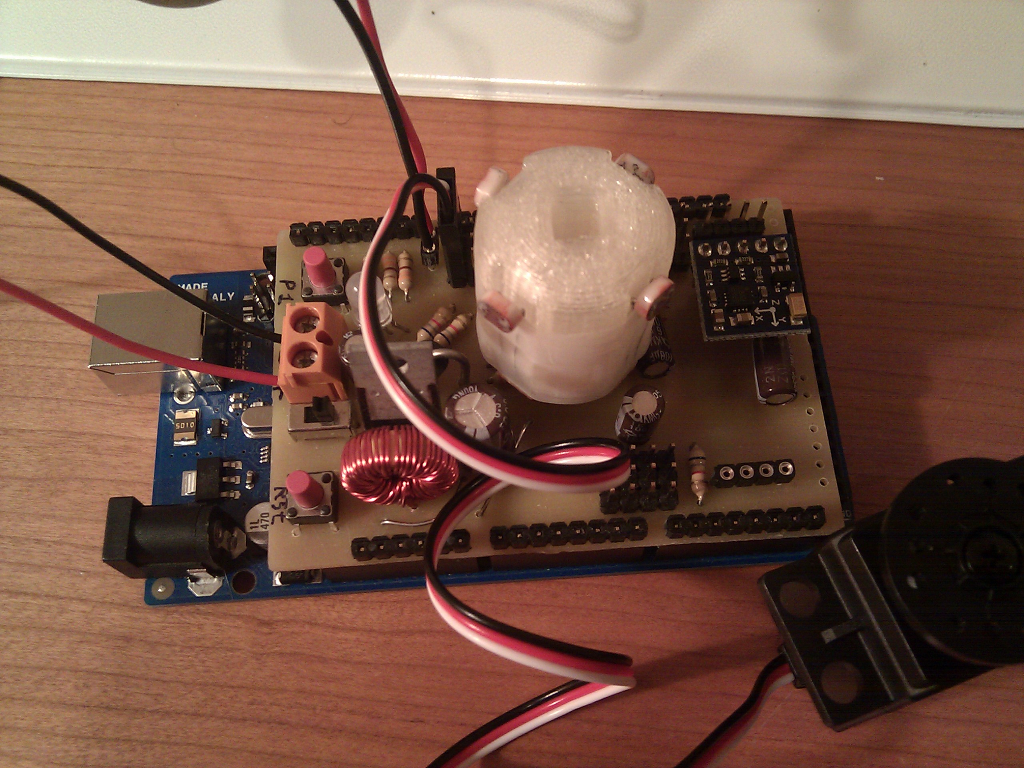
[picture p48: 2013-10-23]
Publications/Media/Robot assembly/2013-08-08 21.00.54.jpg

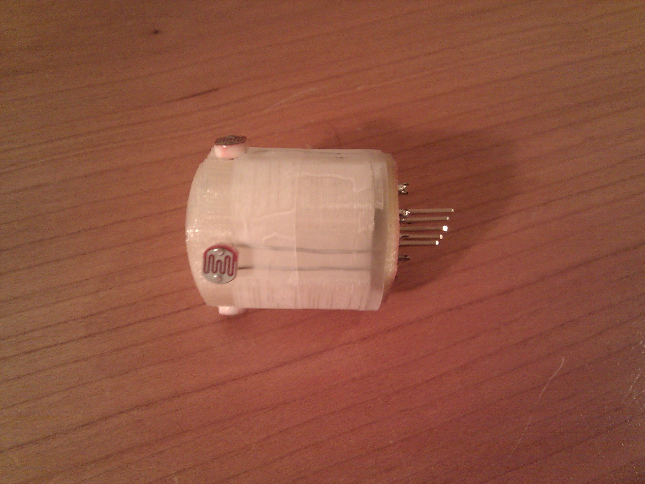
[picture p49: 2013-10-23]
Publications/Media/Robot assembly/2013-08-08 21.00.25.jpg

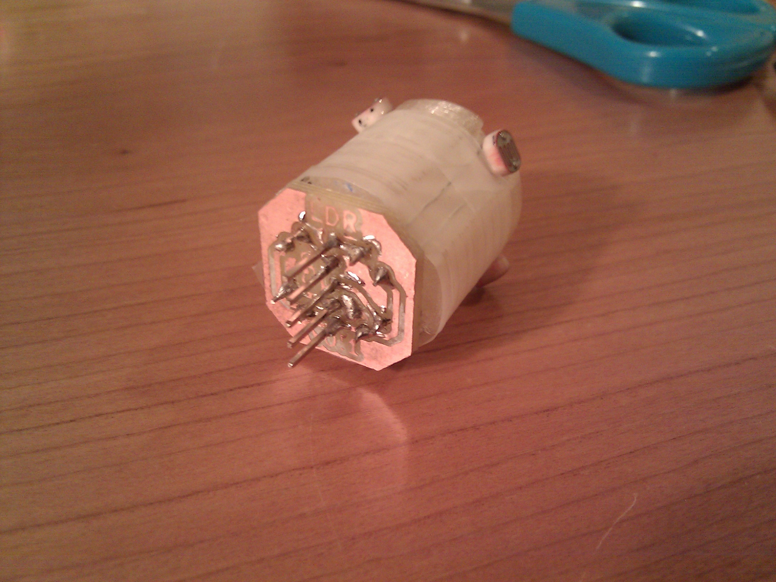
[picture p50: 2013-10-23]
Publications/Media/Robot assembly/2013-08-08 21.00.36.jpg

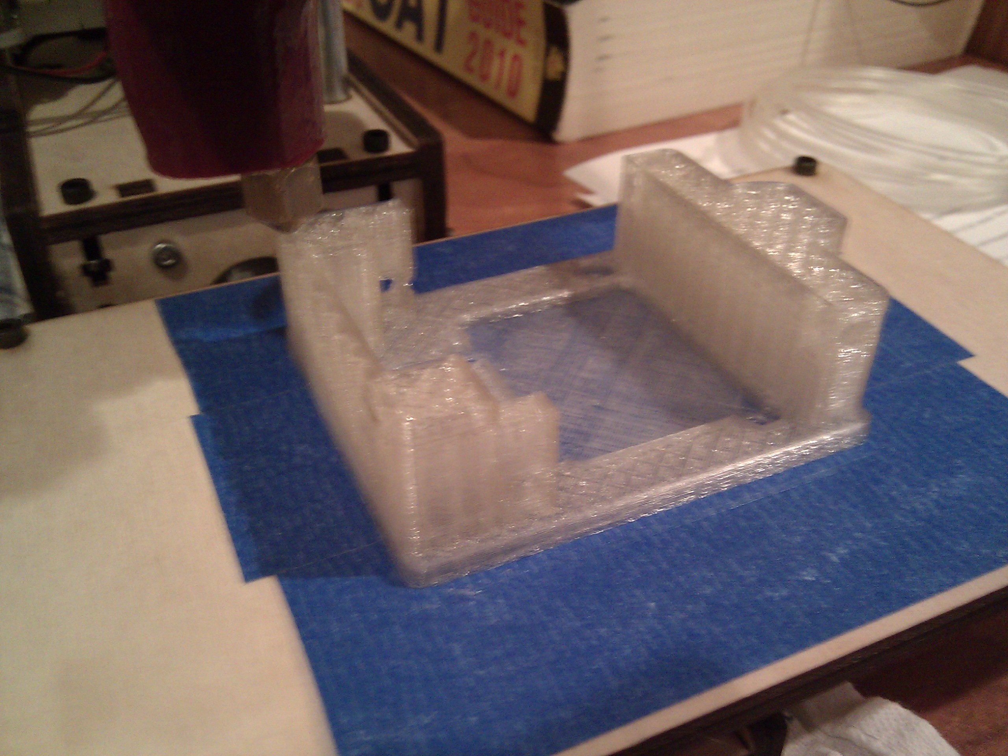
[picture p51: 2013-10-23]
Publications/Media/Robot assembly/2013-08-09 20.21.10.jpg

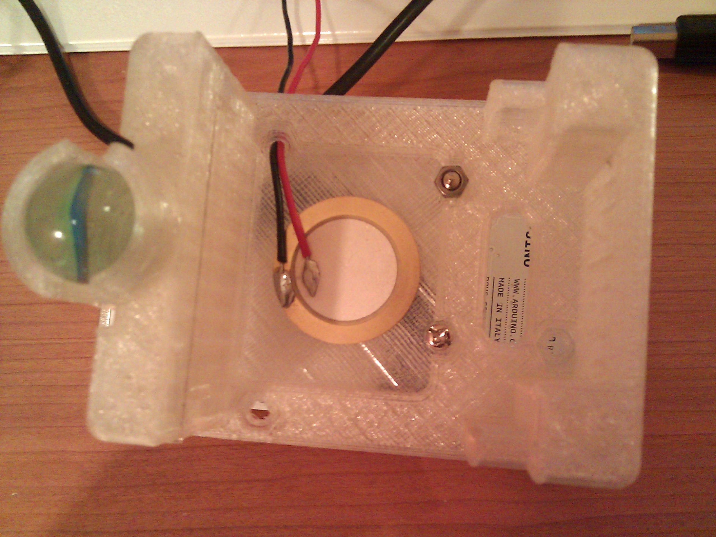
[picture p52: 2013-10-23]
Publications/Media/Robot assembly/2013-08-09 23.04.28.jpg

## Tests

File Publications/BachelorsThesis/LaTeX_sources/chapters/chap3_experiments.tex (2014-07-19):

\chapter{Validation of the developed platform}
\label{chap:experiments}
\vspace{-1cm}

As the GNBot robot and GNBoard electronics have been proposed as a standardized platform for the real-world validation of odor-related search and surveillance tasks, all the implemented functionalities needed to be tested and their performance documented.
This chapter summarizes the results obtained, as well as their implications within the context of future search strategy implementations.

\lsection{Battery life measurements}
\label{sect:batterylife}

Collaborative search algorithms and in particular odor search tasks may require adaptive control of the sensory input in order to maximize sensitivity, and the proper management of actuator elements to reduce energy demand during the exploration.
A first approach can include monitoring events on the battery performance (see Fig. \ref{fig:experiments/battery_performance}) to implement basic decision making on the search strategy.

\begin{figure}[h!]
\centerline{\mbox{}}
\captionFigure{Battery life measurements for distinct average speeds}
{fig:experiments/battery_performance}{
One GNBot powered by two fully-charged 9V 300mAh rechargeable batteries in series configuration was the setup used for this study. A simple obstacle-avoidance routine was used to ensure the continuous motion of the robot.
The cross of curves \emph{b)} and \emph{c)} at $t=100min$ and $t=112min$ shows the variability among the same batch of batteries, and is probably due to differences in charging history.
\emph{Operating time: a) 255min b) 131min c) 119min d) 91min}.
\emph{Distance range estimation: a) 0m b) 90.29m c) 222.26m d) 505.44m}.
}
\end{figure}

The measurements in Figure \ref{fig:experiments/battery_performance} show that servomotors do not have a linear \emph{power/performance} relationship, as they maintain a very high power consumption even at very low speeds. Using this information the search strategy can be adapted to maximize search range. This can be done, for instance, by disabling the motion of the robot when waiting for a sensor measurement to be completed.
The knowledge of various differentiated stages on the battery life is useful information that can be incorporated to trigger a decision-making event during search, to optimize the use of energy resources.
For example, abrupt changes on battery level can trigger a speed change, shutting down high consumption sensors such as the electronic nose, or altering the decision of which robot approaches a given target.
In the case of search strategies based on L\'evy walks, the motion decision extracted from the L\'evy distribution can also be modulated in real time with the battery life estimation.

\lsection{Odor sensing and detection capability}

Apart from bio-inspired energy management, sensing often requires to implement gain control in different sensory modalities to better adapt to variability in each environmental context. Modulation of the temperature of single odor sensors can serve as a virtualization of sensor arrays and it also allows for spatio-temporal encoding which can be needed for more advanced detection and classification tasks. The GNBoard is conveniently provided with the circuitry necessary to achieve this sort of adaptive modulation in odor sensing, and the functionality has been tested to perform as the original \emph{Olus} module (cf. Fig. \ref{fig:introduction/OlusAndTGS2600}).

Whilst odor sensing capability could have been evaluated as a standalone functionality, the multimodal characteristics of robotic search problems make it mandatory to have actual field measurements that demonstrate odor sensing performance. Also, as odor sensing is one of the most characteristic parts of the GNBot design, it is more than convenient to document these features.
Figure \ref{fig:experiments/roomForTests} shows the area utilized for the field odor detection experiments.

\begin{figure}[h!]
\centerline{\mbox{}}
\captionFigure{Room used for the tests (left) and an experiment in progress (right)}
{fig:experiments/roomForTests}{
The chairs were moved to the back of the room before each experiment in order to have free space. Also, the air conditioning system was turned off and all windows were closed to minimize air flow. The picture on the right shows the robot approaching an odor source while the computer-vision algorithm tracks the position of the on-board visual marker.
}
\end{figure}

As each search problem can have a different definition of the characteristics of an odor source, the platform validation tests were performed for two different odor source types (shown in Fig. \ref{fig:experiments/GNBot_and_odorSources}). The evaluation of various odorant targets can also serve to demonstrate the flexibility and easy reconfiguration of the sensors in the robot platform.

\begin{figure}[h!]
\centerline{\mbox{}}
\captionFigure{GNBot and different odor sources}
{fig:experiments/GNBot_and_odorSources}{
The odor source on the left is an open tube containing a 50\% solution of ethanol, which is attached to the ceiling with a wire and suspended at 5cm above the robot. The low-profile target odorant on the right is based on a flat cotton pad impregnated with the same ethanol solution, and contained in a plastic bag with a circular aperture ($D=1cm$) from where the odor plume escapes.
Both odor sources were successfully detected by the GNBot, but the one on the right panel produced more repeatable results as the effect is much more local.
}
\end{figure}

\begin{figure}[h!]
\centerline{\mbox{}}
\captionFigure{Closed-loop robot trajectory over an odor source}
{fig:experiments/linearOdorMap}{
The odor source is adhered to the center of the test area \emph{(b)}.
For the target characterization, the robot performs two passes in opposite directions ($a \rightarrow b \rightarrow c$ and $c \rightarrow b \rightarrow a$). The developed navigation software autonomously commands the robot, closing the control loop with the incorporation of feedback from the visual marker tracking algorithm.
The position of the robot and all sensor measurements are logged in the computer in real time ($T=100ms$).
}
\end{figure}

In order to validate the odor sensing functionality, the decision was to perform basic tests to determine the correlation among the variables \emph{distance to an odor source} and \emph{perceived odor intensity}.
For that purpose, the autonomous navigation capacity of the GNBot was used to execute controlled linear approaches to the odor sources. Figure \ref{fig:experiments/linearOdorMap} describes the methodology of the experiment.

\vspace{-0.3cm}

\subsection{Vision-based robot localization system accuracy}

\vspace{-0.3cm}

Figure \ref{fig:experiments/linearOdorMap} can also be used to ilustrate the autonomous positioning capacity of the developed platform. A camera observing the area of the experiment is controlled by the central computer, where a machine-vision algorithm evaluates the position of each robot in the test environment.
The vision-based system has been possible since high resolution cameras have become low-cost and widely available. The precision in the position and angle measurements is better than $\pm 5cm$, which is quite acceptable, specially when compared to the size of the robots ($10$x$10cm$).
This resolution should be enough for most search algorithm implementations. The system is also highly scalable: placing multiple cameras in the ceiling would allow to monitor larger surfaces without too much overhead in cost.

\vspace{-0.3cm}

\subsection{Odor detection results}

\vspace{-0.3cm}

Characterization results for a low-profile odor source are shown in Figure \ref{fig:experiments/odor_sensor_measurements}.
\begin{figure}[h!]
\centerline{\mbox{}}
\captionFigure{Odor sensor measurements for distinct robot approximation speeds}
{fig:experiments/odor_sensor_measurements}{
Sensor resistance is shown in the top panel, and the actual euclidean distance to the odorant is represented in the bottom.
For the data generation, the robot performs two passes right over the odor source, as shown in Fig. \ref{fig:experiments/linearOdorMap}.
The TGS-2600 gas sensor mounted on board the GNBot works as a resistance whose value varies in relation with the perceived odor intensity.
A reduction of resistance indicates the detection of a significative amount of odorant molecules in air. That way it is possible to identify the presence of an odor source as a falling edge in the resistance of the odor sensor, or with a simple threshold detector (i.e. $R<10k\Omega$).
The double pass of the robot over the odorant allows to determine the hysteresis in sensibility, which is related to the delay needed for normal operation after the saturation of the sensor.
}
\end{figure}
It can be appreciated that odor detection begins for the three cases at around $20cm$ from the odor source, which is the effective range that could be incorporated in search strategies.
The initial hypothesis was that for higher robot velocities the sensor response would be more abrupt, but the obtained results have shown the opposite effect: resistivity reaches lower values for more reduced speeds.
The updated hypothesis is related with the physical characteristics of the TGS-2600 odor sensor, whose sensitivity to odorant concentrations seems to become intensified for longer exposure periods.
Thus, it would be possible to modulate the localization algorithms to adjust the detection threshold according to the velocity of the robot, in order to maximize sensitivity even at high speeds.

Further odor detection tests are detailed in Figure \ref{fig:experiments/5x5reticularMap}. Even with the uncertainty introduced by the use of a suspended odor source rather than a low-profile one, the detection can be successfully achieved.
\begin{figure}[h!]
\centerline{\mbox{}}
\captionFigure{Odor sensor test with a 2-D trajectory}
{fig:experiments/5x5reticularMap}{
For this experiment the navigation algorithm commanded the robot to perform a zig-zag trajectory that combines a set of odor source approximations (see right panel).
The resulting measurements are shown in the left panels: the sensor response (top) and the absolute value of the distance to \emph{c} (bottom).
The suspended odor source in position \emph{c} can be perceived in the measurements even when the robot is near positions \emph{a} and \emph{b} (marked as \emph{``partial detections''}).
Simple threshold detection (i.e. $R<10k\Omega$) applied to the odor sensor response could effectively inform of the presence of the target just before the robot arrival ($t=1min$).
}
\end{figure}

The other factor that can be highlighted from measurements in Figures \ref{fig:experiments/odor_sensor_measurements} and \ref{fig:experiments/5x5reticularMap} is the recovering time -\emph{hysteresis}- of the odor sensor. Whilst the plume detection occurs quite fast, lasting only a few seconds, it can be appreciated that the saturation of the sensor lasts much longer.
For the highest speed result \emph{(c)} in Figure \ref{fig:experiments/odor_sensor_measurements} it is possible to see that in the second pass the sensor has not yet recovered from the previous detection.
This indicates that for an odor search task were multiple odor sources can appear near each other, the monitoring should be performed at slow speeds \emph{(a)} in order to avoid overlaps.

Finally, the rest of multimodal sensors present in the GNBot were also successfully tested: The frontal infra-red distance sensor provides accuracy in the centimeter scale for close-up distances ($10$-$40cm$), and the humidity and temperature sensors provide a resolution of $\pm1\%$ and $\pm0.5\,^{\circ}{\rm C}$ respectively.
The magnetometer module for the electronic compass provided an accuracy of $\pm0.1\,^{\circ}$ after calibration, though magnetic field distortion could be a problem for indoor environments as it is shown in Appendix \ref{Appendix:lightLandmarks}.
Also, wireless communication with the robots via ZigBee did not present any range related limitations and performed as expected from the manufacturer's specification.

\subsection{Easy replication of the GNBot \& four-robot team}

The replicability of the GNBot design was put to test with the creation of four identical robots (shown in Fig. \ref{fig:design/developedPlatform}). Cost was kept very low, at a total of \EUR{600} with an estimated \EUR{150} per robot.
To put the price in perspective, it is important to consider the amount of multimodal sensors present in the robot, as well as the simplistic programming layer with a resilient communication system. The robots also have a long-lasting battery life as it has been shown in \ref{sect:batterylife}.

%\begin{figure}[h!]
%\centerline{\mbox{\includegraphics[width=16cm]{images/GNBot_swarm1.jpg}}}
%\captionFigure{Developed robot swarm}
%{fig:GNBot_swarm1}{
%Four identical GNBot robots equipped with a frontal TGS-2600 odor sensor.
%}
%\end{figure}

Apart from robot validation, the next scientific use for these robots
will be the implementation and real-world validation of a bio-inspired collaborative L\'{e}vy strategy developed at \emph{Grupo de Neurocomputaci\'{o}n Biol\'{o}gica} for the search of multiple odor sources in the environment.
Other strategies will be later on tested and their performance compared in a real environment, all thanks to the presence of the GNBot as a standardized robotic platform.

\newpage 

\begin{figure}[h!]
\centerline{\mbox{}}
\captionFigure{Developed robot platform}
{fig:design/developedPlatform}{
The outcome of the project is a swarm of four remotely-controlled robots that have multimodal sensory input (perceiving light, distance, temperature, humidity and orientation with an electronic compass) and are capable of detecting odor sources such as the low-profile target shown on the left.
These robots are also energy efficient, open-source and easy to expand.
The developed system will allow the implementation of a great variety of cooperative search strategies, including those that use range information from each sensor modality with a characterization of the uncertainty of odor sources, and also the ones that use classical heuristic or brute-force approaches for search. Most importantly, the standardization of the platform could finally provide a fair base of comparison for evaluating differences in efficiency among these odor search strategies.
}\end{figure}

\newpage \thispagestyle{empty} % Página vacía

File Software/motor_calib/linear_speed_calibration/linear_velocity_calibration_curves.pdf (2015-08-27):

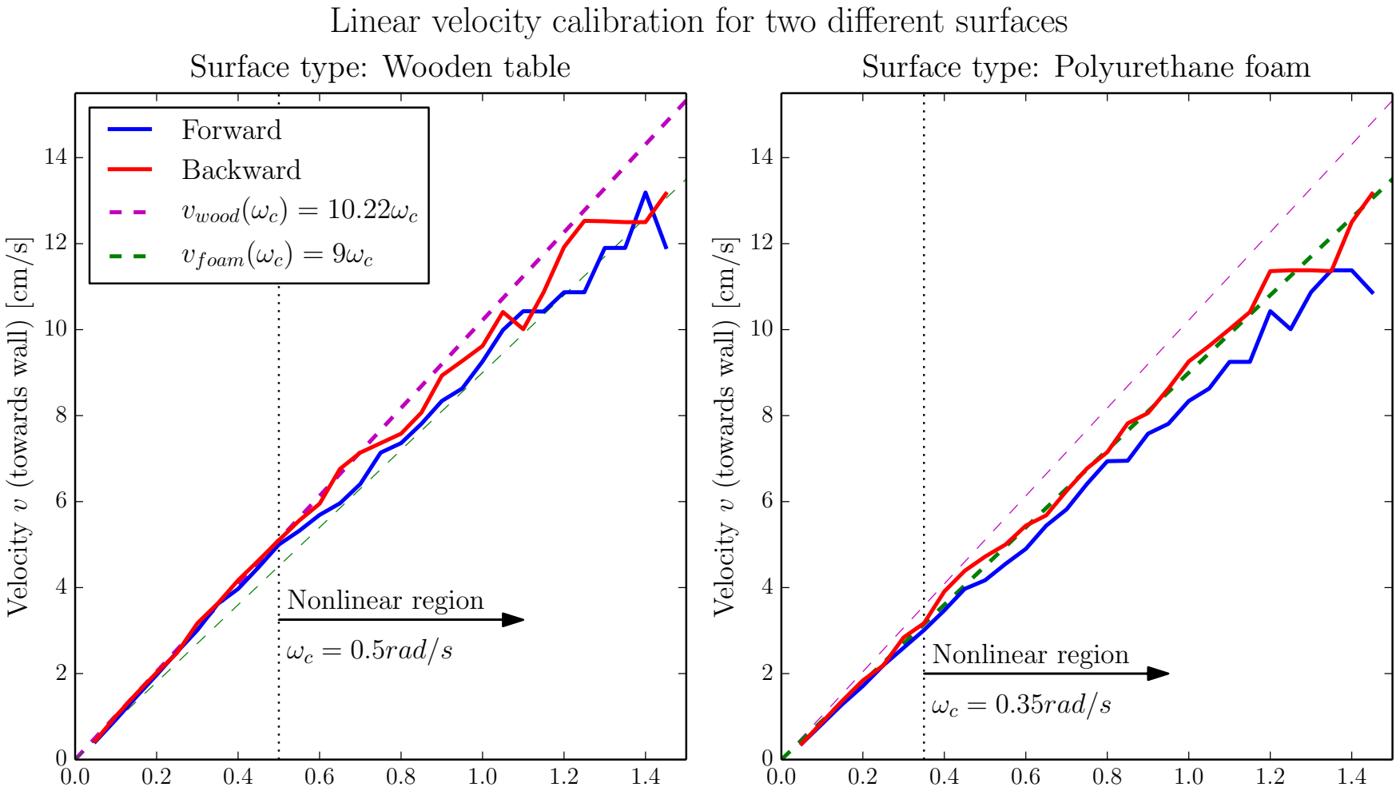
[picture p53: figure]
Velocity; v (towards wall) [cm/s]; ωc = 0.5rad/s; Nonlinear region; Surface type: Wooden table; Forward Backward vwood(ωc) = 10.22ωc; vfoam(ωc) = 9ωc; ωc = 0.35rad/s; Surface type: Polyurethane foam

Motor input rotational velocity ωc [rad/s]

Motor input rotational velocity ωc [rad/s]

### Linear velocity calibration for two different surfaces

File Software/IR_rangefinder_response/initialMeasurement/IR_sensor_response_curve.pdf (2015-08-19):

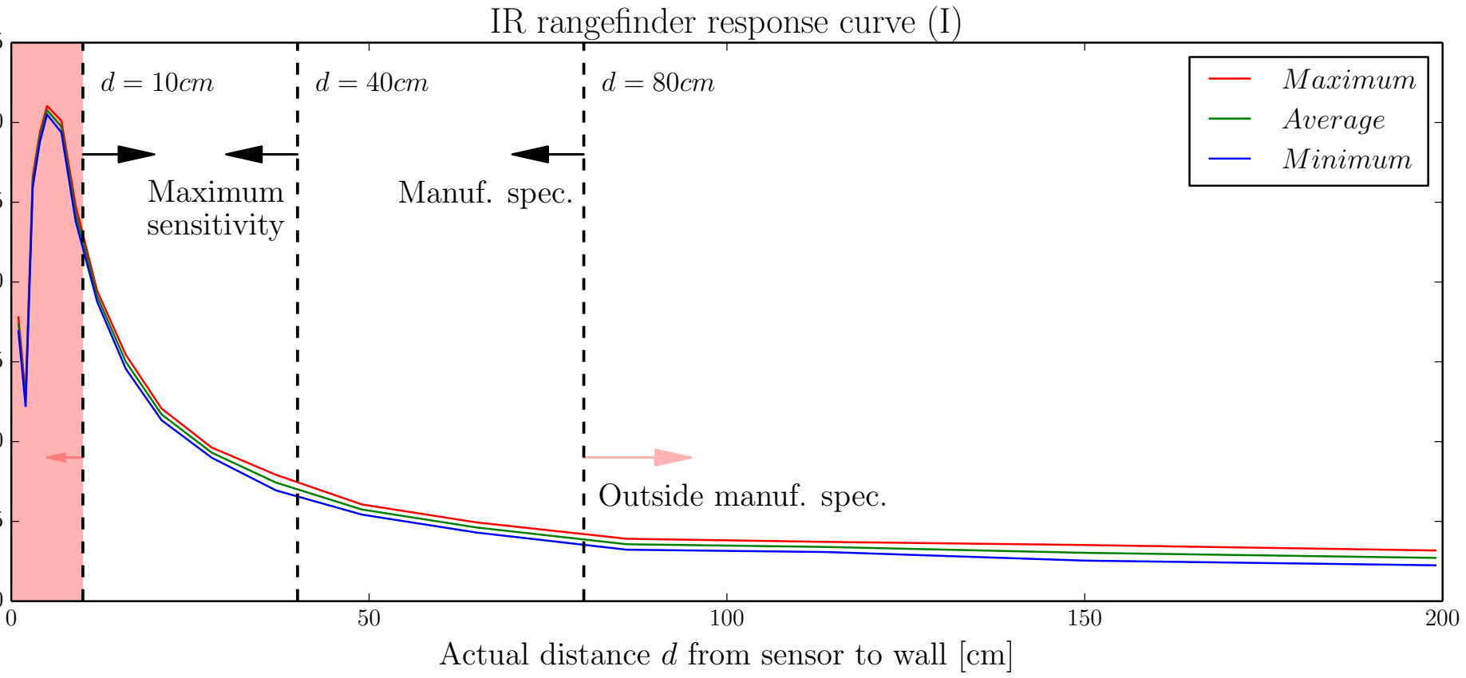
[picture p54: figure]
Actual distance; d from sensor to wall [cm]; Maximum sensitivity; Manuf. spec.; Outside manuf. spec.; IR rangefinder response curve (I); M aximum Average M inimum

0.0 0.5 1.0 1.5 2.0 2.5 3.0 3.5

Sensor output [V]

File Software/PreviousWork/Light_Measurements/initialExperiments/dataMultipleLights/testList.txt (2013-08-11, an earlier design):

Two runs of each, different ambient light

No lights: OK

One light: OK -> LED

Two lights: OK -> LED

Three lights: OK -> 2x LED, 1x Conventional

Four lights: OK -> 2x LED, 2x Conventional

Intensity:
LED lamp: 60
Conventional lamp: 30

Ambient nolights = 20
Ambient lights = 40

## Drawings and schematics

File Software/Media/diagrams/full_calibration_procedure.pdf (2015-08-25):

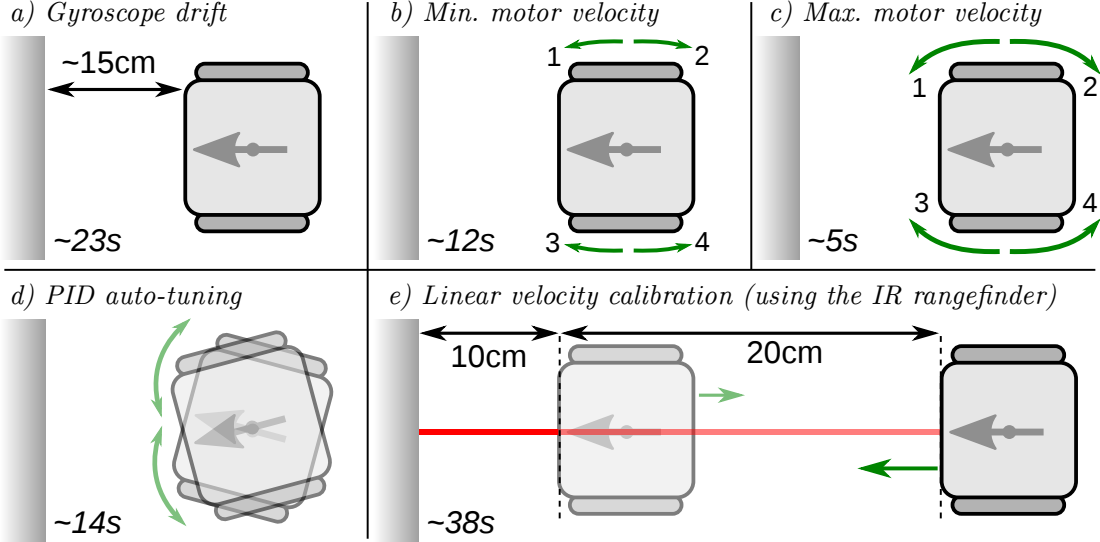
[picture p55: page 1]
a) Gyroscope drift; b) Min. motor velocity; c) Max. motor velocity; d) PID auto-tuning; e) Linear velocity calibration (using the IR rangefinder)

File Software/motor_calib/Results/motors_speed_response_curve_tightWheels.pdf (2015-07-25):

## Motor response curve

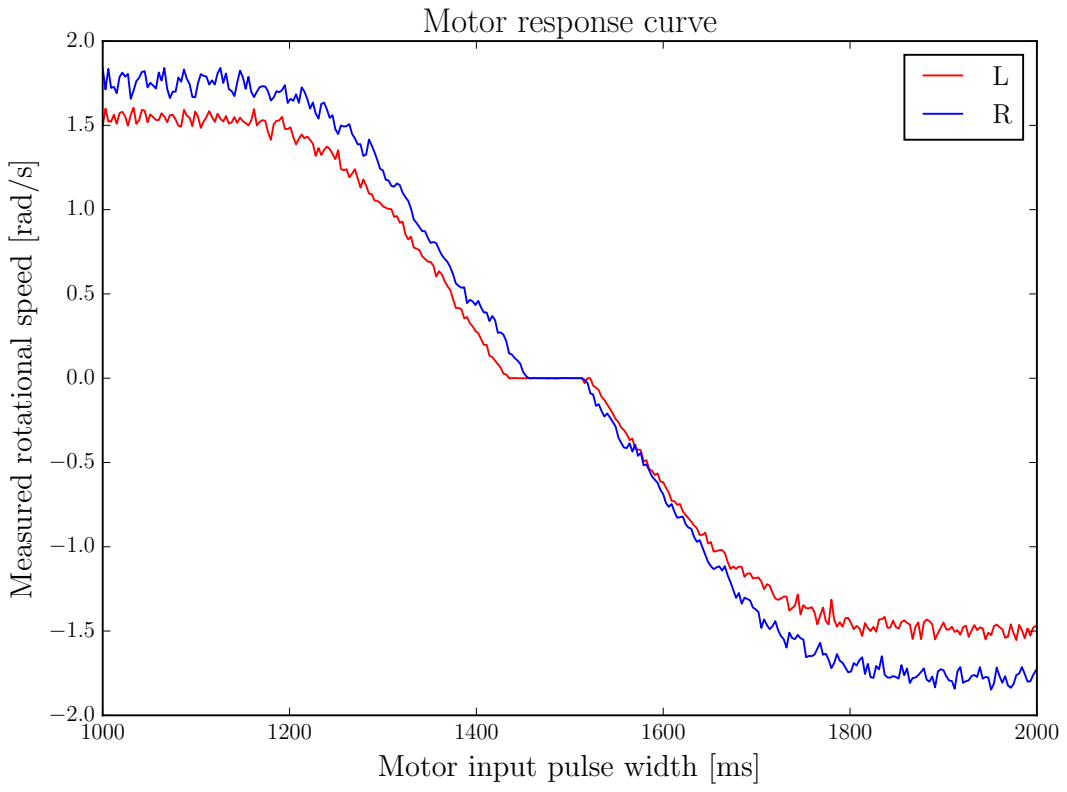
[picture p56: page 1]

Measured rotational speed [rad/s]

Motor input pulse width [ms]

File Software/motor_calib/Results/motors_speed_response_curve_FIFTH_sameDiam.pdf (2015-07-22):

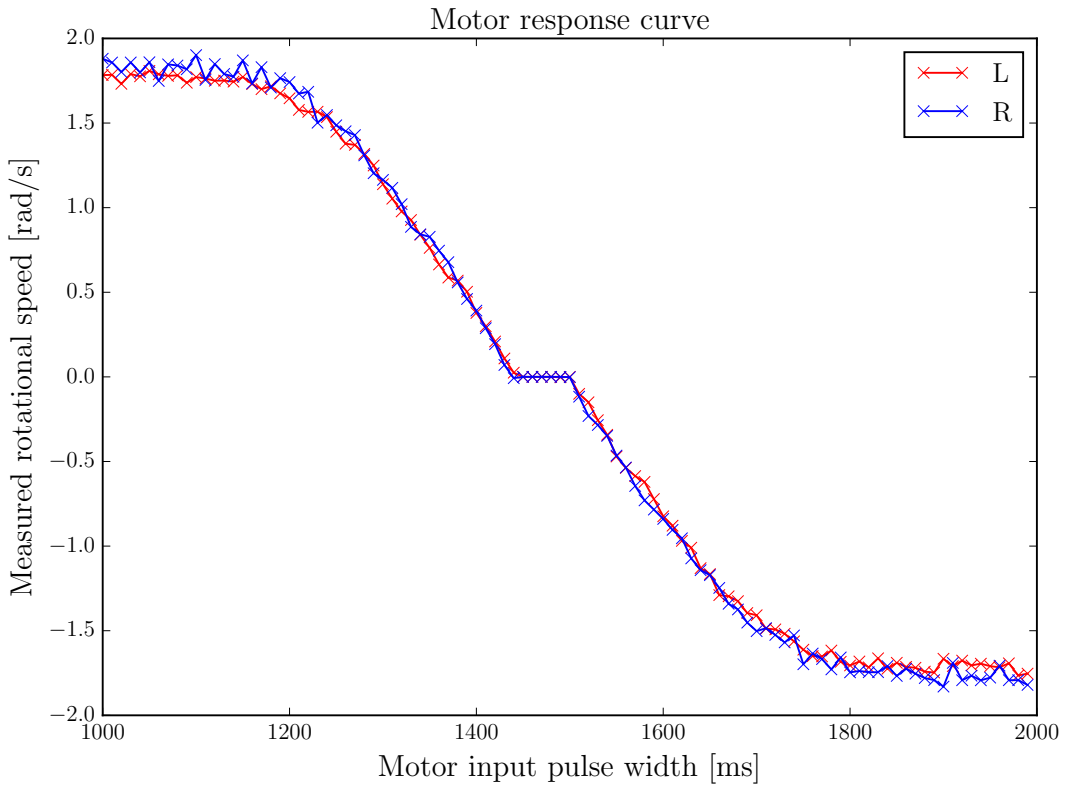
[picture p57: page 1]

Motor response curve

Measured rotational speed [rad/s]

Motor input pulse width [ms]

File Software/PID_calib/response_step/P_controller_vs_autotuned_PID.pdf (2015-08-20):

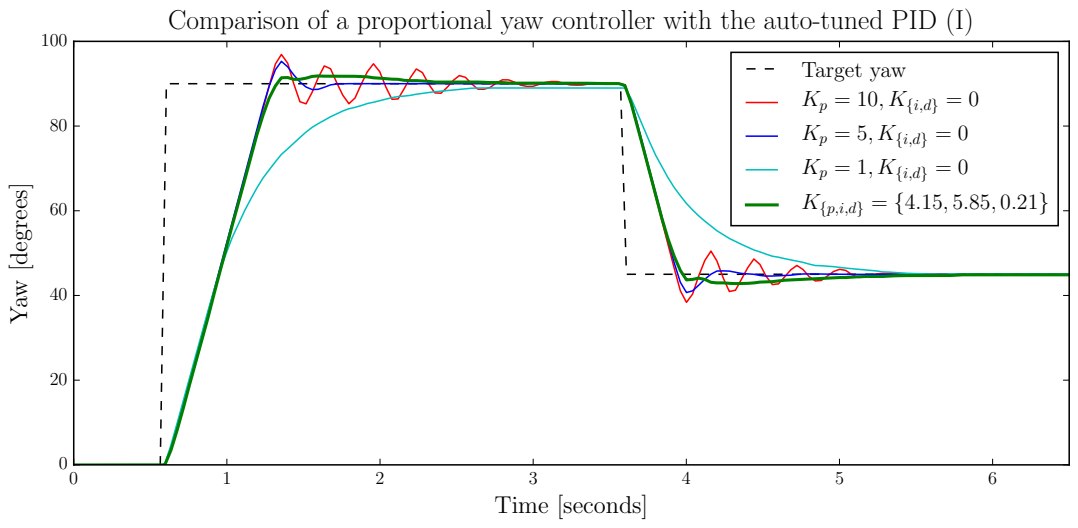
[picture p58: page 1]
Time [seconds]; Yaw [degrees]; Target yaw Kp = 10, K{i,d} = 0

Comparison of a proportional yaw controller with the auto-tuned PID (I)

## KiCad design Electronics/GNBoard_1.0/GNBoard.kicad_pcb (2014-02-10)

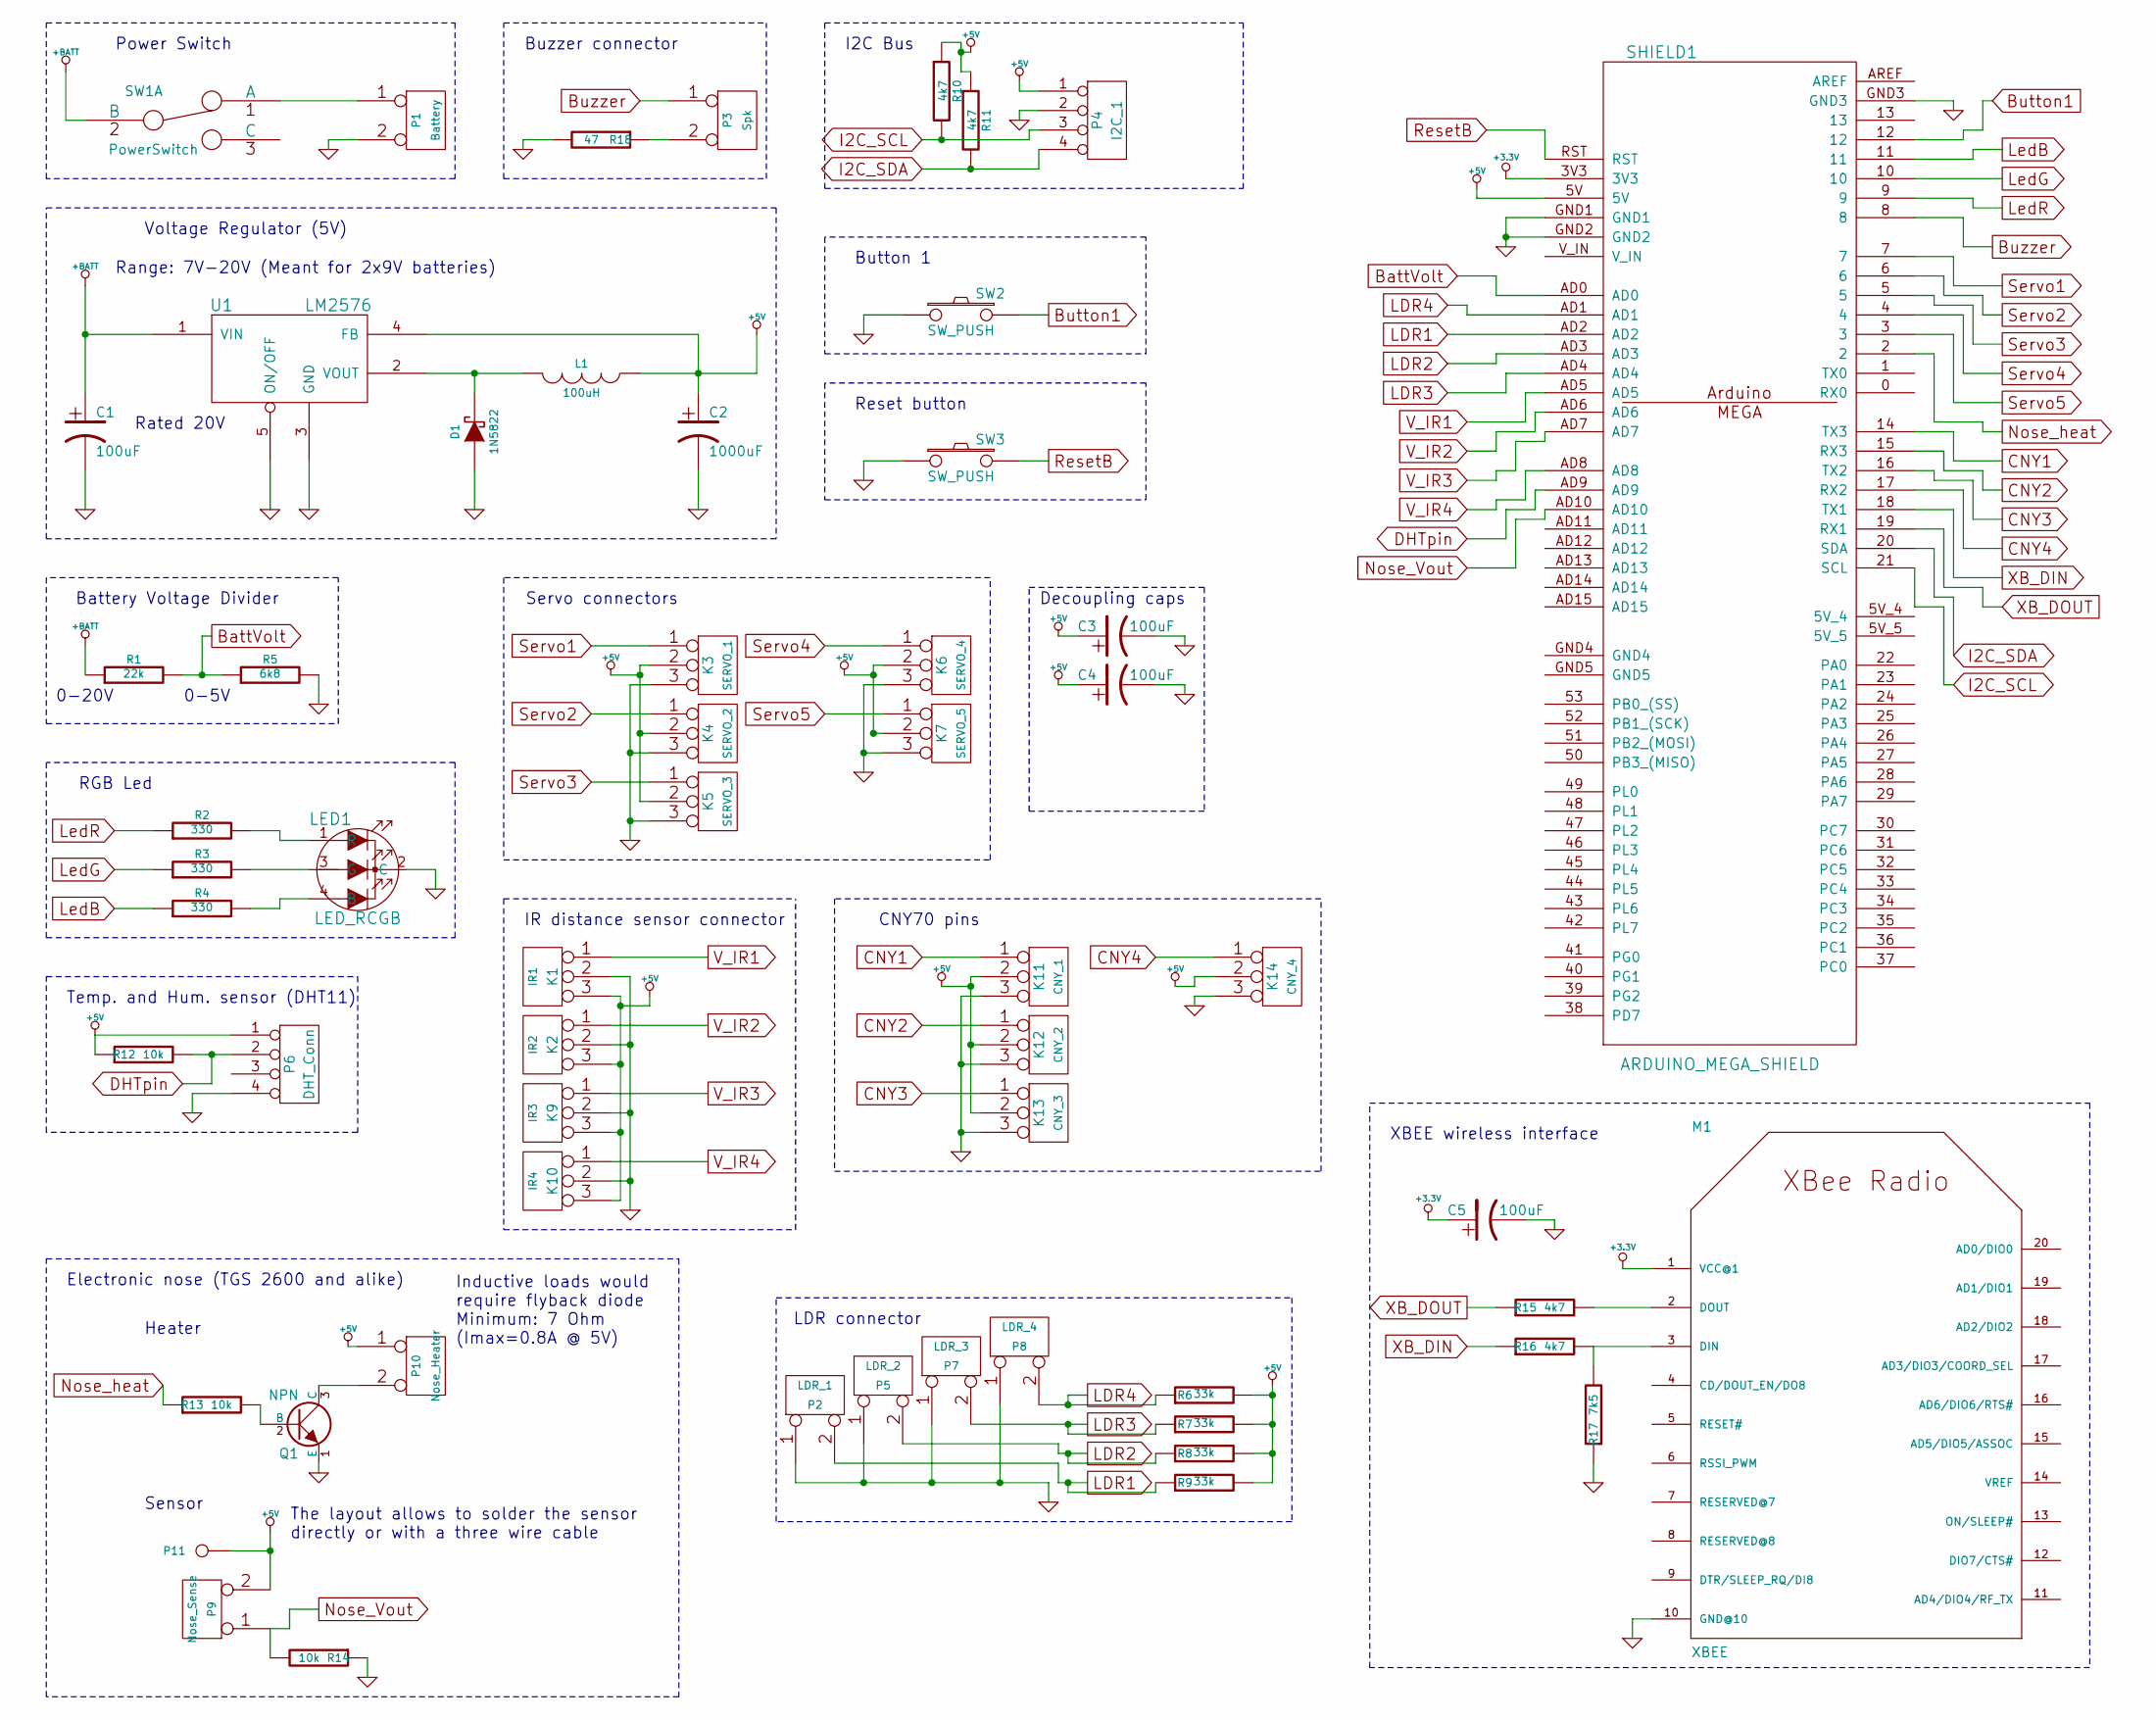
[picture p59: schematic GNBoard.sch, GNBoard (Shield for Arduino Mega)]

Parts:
C1, C3, C4, C5: 100uF
C2: 1000uF
D1: 1N5822
K1: IR1
K2: IR2
K3: SERVO_1
K4: SERVO_2
K5: SERVO_3
K6: SERVO_4
K7: SERVO_5
K9: IR3
K10: IR4
K11: CNY_1
K12: CNY_2
K13: CNY_3
K14: CNY_4
L1: 100uH
LED1: LED_RCGB
M1: XBEE; xbee_r1-XBEE
P1: Battery
P2: LDR_1
P3: Spk
P4: I2C_1
P5: LDR_2
P6: DHT_Conn
P7: LDR_3
P8: LDR_4
P9: Nose_Sense
P10: Nose_Heater
P11: CONN_1
Q1: NPN
R1: 22k
R2, R3, R4: 330
R5: 6k8
R6, R7, R8, R9: 33k
R10, R11, R15, R16: 4k7
R12, R13, R14: 10k
R17: 7k5
R18: 47
SHIELD1: ARDUINO_MEGA_SHIELD
SW1: PowerSwitch
SW2, SW3: SW_PUSH
U1: LM2576

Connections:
+3.3V: C5.1, M1.1 (VCC@1), SHIELD1.3V3
+5V: C2.1, C3.1, C4.1, K1.3, K2.3, K3.2 (PM), K4.2 (PM), K5.2 (PM), K6.2 (PM), K7.2 (PM), K9.3, K10.3, K11.2 (PM), K12.2 (PM), K13.2 (PM), K14.2 (PM), L1.1, P4.1, P6.1, P9.2 (PM), P10.1, P11.1, R6.2, R7.2, R8.2, R9.2, R10.1, R11.1, R12.1, SHIELD1.5V, U1.4 (FB)
+BATT: C1.1, R1.1, SW1.2 (B), U1.1 (VIN)
BattVolt: R1.2, R5.1, SHIELD1.AD0
Button1: SHIELD1.12, SW2.2
Buzzer: P3.1, SHIELD1.8
CNY1: K11.1, SHIELD1.14 (TX3)
CNY2: K12.1, SHIELD1.15 (RX3)
CNY3: K13.1, SHIELD1.16 (TX2)
CNY4: K14.1, SHIELD1.17 (RX2)
DHTpin: P6.2, R12.2, SHIELD1.AD9
GND: C1.2, C2.2, C3.2, C4.2, C5.2, D1.1 (A), K1.2 (PM), K2.2 (PM), K3.3, K4.3, K5.3, K6.3, K7.3, K9.2 (PM), K10.2 (PM), K11.3, K12.3, K13.3, K14.3, LED1.2 (C), M1.10 (GND@10), P1.2 (PM), P2.1, P4.2, P5.1, P6.4, P7.1, P8.1, Q1.1 (E), R5.2, R14.1, R17.1, R18.2, SHIELD1.GND1, SHIELD1.GND2, SHIELD1.GND3, SW2.1, SW3.1, U1.3 (GND), U1.5 (ON/OFF)
I2C_SCL: P4.3, R10.2, SHIELD1.21 (SCL)
I2C_SDA: P4.4, R11.2, SHIELD1.20 (SDA)
LDR1: P2.2 (PM), R9.1, SHIELD1.AD2
LDR2: P5.2 (PM), R8.1, SHIELD1.AD3
LDR3: P7.2 (PM), R7.1, SHIELD1.AD4
LDR4: P8.2 (PM), R6.1, SHIELD1.AD1
LedB: R4.1, SHIELD1.11
LedG: R3.1, SHIELD1.10
LedR: R2.1, SHIELD1.9
unnamed: LED1.3 (G), R3.2
unnamed: P3.2 (PM), R18.1
unnamed: LED1.4 (B), R4.2
unnamed: LED1.1 (R), R2.2
unnamed: D1.2 (K), L1.2, U1.2 (VOUT)
unnamed: P1.1, SW1.1 (A)
unnamed: M1.3 (DIN), R16.2, R17.2
unnamed: M1.2 (DOUT), R15.2
unnamed: Q1.2 (B), R13.2
unnamed: P10.2 (PM), Q1.3 (C)
Nose_Vout: P9.1, R14.2, SHIELD1.AD10
Nose_heat: R13.1, SHIELD1.2
ResetB: SHIELD1.RST, SW3.2
Servo1: K3.1, SHIELD1.7
Servo2: K4.1, SHIELD1.6
Servo3: K5.1, SHIELD1.5
Servo4: K6.1, SHIELD1.4
Servo5: K7.1, SHIELD1.3
V_IR1: K1.1, SHIELD1.AD5
V_IR2: K2.1, SHIELD1.AD6
V_IR3: K9.1, SHIELD1.AD7
V_IR4: K10.1, SHIELD1.AD8
XB_DIN: R16.1, SHIELD1.18 (TX1)
XB_DOUT: R15.1, SHIELD1.19 (RX1)

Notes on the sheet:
Voltage Regulator (5V)
RGB Led
Battery Voltage Divider
Power Switch
LDR connector
IR distance sensor connector
Servo connectors
CNY70 pins
Buzzer connector
Reset button
I2C Bus
Button 1
Temp. and Hum. sensor (DHT11)
Decoupling caps
Range: 7V-20V (Meant for 2x9V batteries)
Rated 20V
0-5V
0-20V
Electronic nose (TGS 2600 and alike)
XBEE wireless interface
Inductive loads would require flyback diode Minimum: 7 Ohm (Imax=0.8A @ 5V)
Heater
Sensor
The layout allows to solder the sensor directly or with a three wire cable

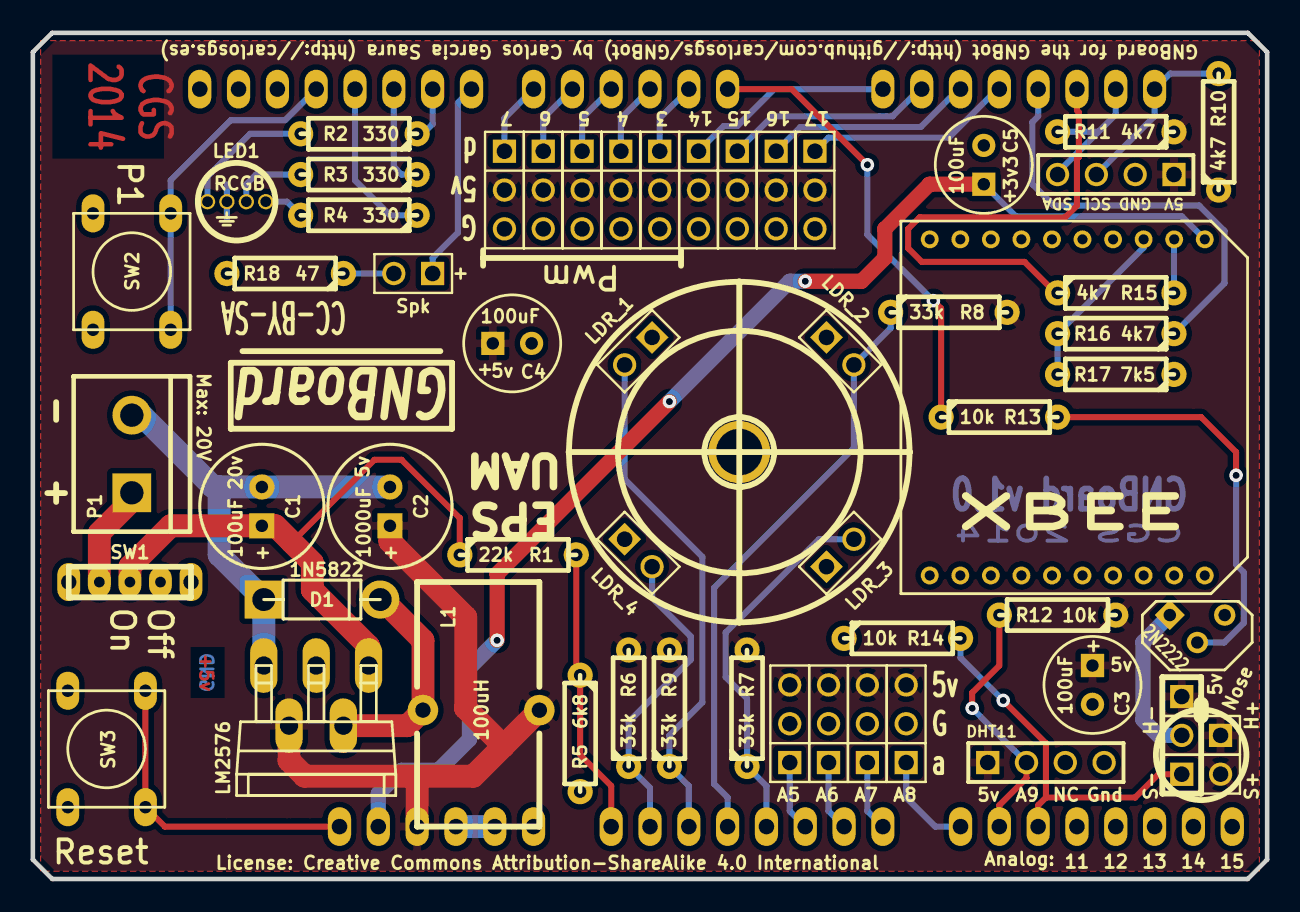
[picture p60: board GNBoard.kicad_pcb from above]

Board: 2 copper layers, 80.8 x 55.4 mm, 58 parts (0 on the bottom side), 45 nets.

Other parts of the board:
1PIN: P***; ldr_drill

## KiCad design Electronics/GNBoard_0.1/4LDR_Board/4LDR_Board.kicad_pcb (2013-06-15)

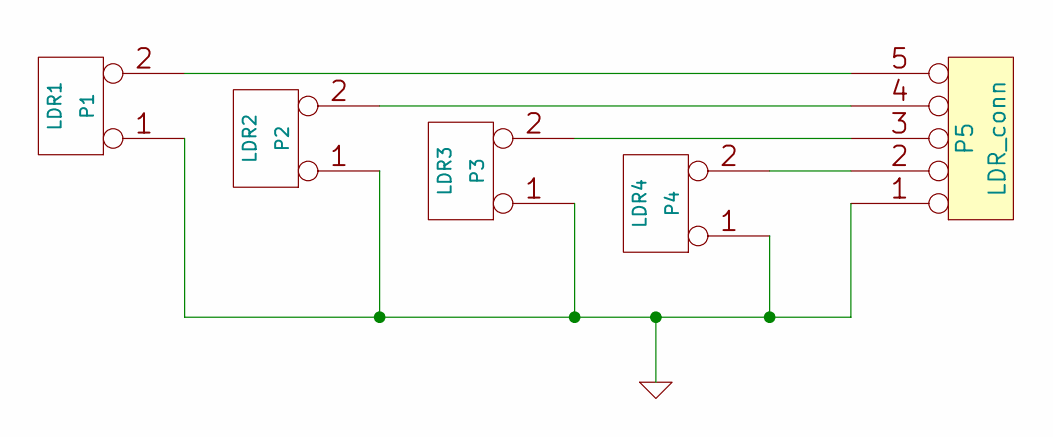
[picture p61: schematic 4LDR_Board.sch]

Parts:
P1: LDR1
P2: LDR2
P3: LDR3
P4: LDR4
P5: LDR_conn

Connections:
GND: P1.1, P2.1, P3.1, P4.1, P5.1
unnamed: P2.2 (PM), P5.4
unnamed: P1.2 (PM), P5.5
unnamed: P3.2 (PM), P5.3
unnamed: P4.2 (PM), P5.2

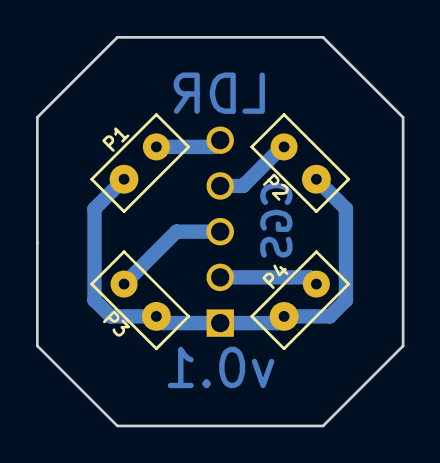
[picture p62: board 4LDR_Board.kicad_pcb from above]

Board: 2 copper layers, 20.3 x 21.6 mm, 5 parts (1 on the bottom side), 5 nets.

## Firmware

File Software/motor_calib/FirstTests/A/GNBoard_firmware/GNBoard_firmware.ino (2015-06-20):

// GNBoard Firmware by Carlosgs (http://carlosgs.es)
// License: CC-BY-SA (http://creativecommons.org/licenses/by-sa/3.0/)

#include <Servo.h>
#include <Wire.h> //I2C Arduino Library
#include <HMC5883L.h> //Compass library
#include <XBee.h> // XBee library (usage based on examples by Andrew Rapp)
#include <dht11.h>

// create the XBee object
XBee xbee = XBee();

// create the DHT11 object (sensor for temperature and humidity)
dht11 DHT11;

#define XbeeSerial Serial1

#define Serial Serial

#define NOSE_HEAT_PIN 2
#define NOSE_VOUT_PIN A10

#define LDR1_PIN A2
#define LDR2_PIN A3
#define LDR3_PIN A4
#define LDR4_PIN A1

#define IR1_PIN A5
#define IR2_PIN A6
#define IR3_PIN A7
#define IR4_PIN A8

#define LED_R_PIN 9
#define LED_G_PIN 10
#define LED_B_PIN 11

#define BATTERY_PIN A0

#define BUTTON_1_PIN 12

#define DHT_PIN A9

#define BUZZER_PIN 8

#define SERVO_1_PIN 7 // left
#define SERVO_2_PIN 6 // right

Servo Servo1;
Servo Servo2;


float mapf(float x, float in_min, float in_max, float out_min, float out_max)
{
  return (x - in_min) * (out_max - out_min) / (in_max - in_min) + out_min;
}

// IMU
#include "I2Cdev.h"
#include "MPU6050_6Axis_MotionApps20.h"
#if I2CDEV_IMPLEMENTATION == I2CDEV_ARDUINO_WIRE
    #include "Wire.h"
#endif
MPU6050 mpu;

// MPU control/status vars
bool dmpReady = false;  // set true if DMP init was successful
uint8_t mpuIntStatus;   // holds actual interrupt status byte from MPU
uint16_t packetSize;    // expected DMP packet size (default is 42 bytes)
uint16_t fifoCount;     // count of all bytes currently in FIFO
uint8_t fifoBuffer[64]; // FIFO storage buffer

// orientation/motion vars
Quaternion q;           // [w, x, y, z]         quaternion container
VectorFloat gravity;    // [x, y, z]            gravity vector
float ypr[3];           // [yaw, pitch, roll]   yaw/pitch/roll container and gravity vector

void setupIMU() {
    // join I2C bus (I2Cdev library doesn't do this automatically)
    #if I2CDEV_IMPLEMENTATION == I2CDEV_ARDUINO_WIRE
        Wire.begin();
        TWBR = 24; // 400kHz I2C clock (200kHz if CPU is 8MHz)
    #elif I2CDEV_IMPLEMENTATION == I2CDEV_BUILTIN_FASTWIRE
        Fastwire::setup(400, true);
    #endif
    
    
    mpu.initialize();
    
    delay(100);
    
    uint8_t devStatus = mpu.dmpInitialize(); //(0 = success, !0 = error)
    
    
    // Calibration offsets
    mpu.setXGyroOffset(34);
    mpu.setYGyroOffset(-26);
    mpu.setZGyroOffset(24);
//    mpu.setZAccelOffset(1788);
    
    
    if (devStatus == 0) {
        //mpu.setRate(4); // 1khz / (1 + 4) = 200 Hz
        mpu.setDMPEnabled(true);
        mpuIntStatus = mpu.getIntStatus();
        // get expected DMP packet size for later comparison
        packetSize = mpu.dmpGetFIFOPacketSize();
        dmpReady = true;
    }
}


// Magnetometer
// Store our compass as a variable.
HMC5883L compass;
float declinationAngle = 0;
float compass_yMax = -1;
float compass_yMin = 1;
float compass_xMax = -1;
float compass_xMin = 1;
float readMagnetometer() {
  MagnetometerRaw raw = compass.ReadRawAxis();
  return raw.XAxis;
  // Retrived the scaled values from the compass (scaled to the configured scale).
  MagnetometerScaled scaled = compass.ReadScaledAxis();
  if(scaled.YAxis > compass_yMax)
    compass_yMax = scaled.YAxis;
  if(scaled.YAxis < compass_yMin)
    compass_yMin = scaled.YAxis;
  if(scaled.XAxis > compass_xMax)
    compass_xMax = scaled.XAxis;
  if(scaled.XAxis < compass_xMin)
    compass_xMin = scaled.XAxis;
  float y = mapf(scaled.YAxis, compass_yMin, compass_yMax, -1, 1);
  float x = mapf(scaled.XAxis, compass_xMin, compass_xMax, -1, 1);
  float heading = atan2(y, x);
  return scaled.XAxis;
  Serial.print("YAxis:");
  Serial.print(scaled.YAxis);
  Serial.print("YAxis:");
  Serial.println(scaled.YAxis);

  // Once you have your heading, you must then add your 'Declination Angle', which is the 'compassError' of the magnetic field in your location.
  // Find yours here: http://www.magnetic-declination.com/
  // Mine is: 2'' 37' W, which is 2.617 Degrees, or (which we need) 0.0456752665 radians, I will use 0.0457
  // If you cannot find your Declination, comment out these two lines, your compass will be slightly off.
  //float declinationAngle = 0;
  heading += declinationAngle;

  // Correct for when signs are reversed.
  if(heading < 0)
    heading += 2*PI;

  // Check for wrap due to addition of declination.
  if(heading > 2*PI)
    heading -= 2*PI;

  // Convert radians to degrees for readability.
  float headingDegrees = heading * 180/M_PI;
  return headingDegrees;
}
// Record any compassErrors that may occur in the compass.
int compassError = 0;
void magnetometerToZero() {
  // Set our initial offset angle
  MagnetometerScaled scaled = compass.ReadScaledAxis();
  float heading = atan2(scaled.YAxis, scaled.XAxis);
  declinationAngle = -heading;
}
void setupMagnetometer() {
  Serial.println("Starting the I2C interface.");
  Wire.begin(); // Start the I2C interface.

  Serial.println("Constructing new HMC5883L");
  compass = HMC5883L(); // Construct a new HMC5883 compass.

  Serial.println("Setting scale to +/- 1.3 Ga");
  compassError = compass.SetScale(0.88); // Set the scale of the compass.
  if(compassError != 0) // If there is an compassError, print it out.
    Serial.println(compass.GetErrorText(compassError));

  Serial.println("Setting measurement mode to continous.");
  compassError = compass.SetMeasurementMode(Measurement_Continuous); // Set the measurement mode to Continuous
  if(compassError != 0) // If there is an compassError, print it out.
    Serial.println(compass.GetErrorText(compassError));

  // Set our initial offset angle
  magnetometerToZero();
}

// Music notes
#define DO 262
#define RE 294
#define MI 330
#define FA 349
#define SOL 392
#define LA 440
#define SI 494

int frequencies[] = {
  DO,RE,MI,FA,SOL,LA,SI};

void playNote(int frequency, int length) {
  if(frequency <= 0) frequency = DO;
  if(length <= 0) length = 100;
  tone(BUZZER_PIN,frequency);
  delay(length);
  noTone(BUZZER_PIN);
  delay(100);
}

void playMusicScale(int length) {
  playNote(DO, length);
  playNote(RE, length);
  playNote(MI, length);
  playNote(FA, length);
  playNote(SOL, length);
  playNote(LA, length);
  playNote(SI, length);
}

void playInvertedMusicScale(int length) {
  playNote(SI, length);
  playNote(LA, length);
  playNote(SOL, length);
  playNote(FA, length);
  playNote(MI, length);
  playNote(RE, length);
  playNote(DO, length);
}

void playMusicTone1(int length) {
  playNote(MI, length);
  playNote(DO, length);
  playNote(MI, length);
  playNote(DO, length);
  playNote(DO, length);
  playNote(DO, length);
  playNote(DO, length*3);
}


// --- BUTTON ---

// Function for initiating the pin used by the button
void init_button_pin() {
  pinMode(BUTTON_1_PIN,INPUT);

  digitalWrite(BUTTON_1_PIN, HIGH); // Enable internal pull-up resistor
}

// Function for reading the button value
// Returns 1 if the button is being pressed, 0 if it is not
int button_is_pressed() {
  return !digitalRead(BUTTON_1_PIN);
}

// Function that waits until the button is pressed
void wait_for_button_press() {
  while( button_is_pressed() == 0 ) {
    delay(100);
  }
}



void ledColor(int R, int G, int B) {
  analogWrite(LED_R_PIN, R);
  analogWrite(LED_G_PIN, G);
  analogWrite(LED_B_PIN, B);
}

void ledRandom(int maxVal) {
  ledColor(random(maxVal+1),random(maxVal+1),random(maxVal+1));
}

int servo1pos = 90,servo1inc=1;
int servo2pos = 90,servo2inc=-2;

unsigned long iniTime;
unsigned long currTime;
unsigned long last_timestamp = 0;

unsigned long last_timestamp_DHT11 = 0;

int loggerMode = 0;

void initRobot() {

  init_button_pin();

  Servo1.write(90);
  Servo2.write(90);

  magnetometerToZero();

  loggerMode = 0;

  playMusicScale(20);
}







float analogReadAverage(int pin, int samples) {
  int result = 0;
  for(int i=0; i<samples; i++) {
    result += analogRead(pin);
  }
  return float(result)/float(samples);
}

float getDistanceCM() {
  float measurement = analogReadAverage(IR4_PIN,4);
  float ir_K = 4244.64;
  float ir_C = 37.28;
  return ir_K/(measurement-ir_C);
}

float getBatteryVoltage() {
  int val = analogRead(BATTERY_PIN);
  return mapf(val,0,1023, 0,21.1765); // Voltage divider with 22k in series with 6k8
}

char inBuffer[128] = "";
int inBuffer_len = 0;

void readLine(char *out) {
  int gotLine = 0;
  while(Serial.available()) {
    char val = Serial.read();
    if(val == '\n') {
      gotLine = 1;
      break;
    }
    if(val != '\r') {
      inBuffer[inBuffer_len] = val;
      inBuffer_len++;
      //char strVal[2];
      //strVal[0] = val;
      //strVal[1] = '\0';
      //strcat(inBuffer,strVal);
    }
  }
  if(gotLine) {
    inBuffer[inBuffer_len] = '\0';
    strcpy(out,inBuffer);
    //*inBuffer = '\0';
    inBuffer_len = 0;
  } 
  else
    *out = '\0';
}

char buffer[128];

int motors_oldL = 90;
int motors_oldR = 90;


int statusLed = LED_G_PIN;
int errorLed = LED_R_PIN;
void flashLed(int pin, int times, int wait) {

  for (int i = 0; i < times; i++) {
    digitalWrite(pin, HIGH);
    delay(wait);
    digitalWrite(pin, LOW);

    if (i + 1 < times) {
      delay(wait);
    }
  }
}
ZBTxStatusResponse txStatus = ZBTxStatusResponse();

// Modified from http://www.desert-home.com/2013/02/using-xbee-library-part-3.html
XBeeAddress64 CoordinatorAddress = XBeeAddress64(0x00000000, 0x00000000); // Address 0 is the coordinator
void sendXbee(const char* command, int len){
  ZBTxRequest zbtx = ZBTxRequest(CoordinatorAddress, (uint8_t *)command, len);
  xbee.send(zbtx);
}

ZBRxResponse rx = ZBRxResponse();




unsigned int imu_yaw_tushort;
unsigned int imu_pitch_tushort;
unsigned int imu_roll_tushort;
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

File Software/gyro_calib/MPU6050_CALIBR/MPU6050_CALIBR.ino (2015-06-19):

// I2C device class (I2Cdev) demonstration Arduino sketch for MPU6050 class
// 10/7/2011 by Jeff Rowberg <jeff@rowberg.net>
// Updates should (hopefully) always be available at https://github.com/jrowberg/i2cdevlib
//
// Changelog:
//      2013-05-08 - added multiple output formats
//                 - added seamless Fastwire support
//      2011-10-07 - initial release

/* ============================================
I2Cdev device library code is placed under the MIT license
Copyright (c) 2011 Jeff Rowberg

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
THE SOFTWARE IS PROVIDED "AS IS", WITHOUT WARRANTY OF ANY KIND, EXPRESS OR
IMPLIED, INCLUDING BUT NOT LIMITED TO THE WARRANTIES OF MERCHANTABILITY,
FITNESS FOR A PARTICULAR PURPOSE AND NONINFRINGEMENT. IN NO EVENT SHALL THE
AUTHORS OR COPYRIGHT HOLDERS BE LIABLE FOR ANY CLAIM, DAMAGES OR OTHER
LIABILITY, WHETHER IN AN ACTION OF CONTRACT, TORT OR OTHERWISE, ARISING FROM,
OUT OF OR IN CONNECTION WITH THE SOFTWARE OR THE USE OR OTHER DEALINGS IN
THE SOFTWARE.
===============================================
*/

// I2Cdev and MPU6050 must be installed as libraries, or else the .cpp/.h files
// for both classes must be in the include path of your project
#include "I2Cdev.h"
#include "MPU6050.h"

// Arduino Wire library is required if I2Cdev I2CDEV_ARDUINO_WIRE implementation
// is used in I2Cdev.h
#if I2CDEV_IMPLEMENTATION == I2CDEV_ARDUINO_WIRE
    #include "Wire.h"
#endif

// class default I2C address is 0x68
// specific I2C addresses may be passed as a parameter here
// AD0 low = 0x68 (default for InvenSense evaluation board)
// AD0 high = 0x69
MPU6050 accelgyro;
//MPU6050 accelgyro(0x69); // <-- use for AD0 high

int16_t ax, ay, az;
int16_t gx, gy, gz;

int16_t axf, ayf, azf;
int16_t gxf, gyf, gzf;


// uncomment "OUTPUT_READABLE_ACCELGYRO" if you want to see a tab-separated
// list of the accel X/Y/Z and then gyro X/Y/Z values in decimal. Easy to read,
// not so easy to parse, and slow(er) over UART.
#define OUTPUT_READABLE_ACCELGYRO

// uncomment "OUTPUT_BINARY_ACCELGYRO" to send all 6 axes of data as 16-bit
// binary, one right after the other. This is very fast (as fast as possible
// without compression or data loss), and easy to parse, but impossible to read
// for a human.
//#define OUTPUT_BINARY_ACCELGYRO

#define BUTTON_1_PIN 12


// --- BUTTON ---

// Function for initiating the pin used by the button
void init_button_pin() {
  pinMode(BUTTON_1_PIN,INPUT);

  digitalWrite(BUTTON_1_PIN, HIGH); // Enable internal pull-up resistor
}

// Function for reading the button value
// Returns 1 if the button is being pressed, 0 if it is not
int button_is_pressed() {
  return !digitalRead(BUTTON_1_PIN);
}





#define LED_PIN 13
bool blinkState = false;

void setup() {
    // join I2C bus (I2Cdev library doesn't do this automatically)
    #if I2CDEV_IMPLEMENTATION == I2CDEV_ARDUINO_WIRE
        Wire.begin();
    #elif I2CDEV_IMPLEMENTATION == I2CDEV_BUILTIN_FASTWIRE
        Fastwire::setup(400, true);
    #endif

    // initialize serial communication
    // (38400 chosen because it works as well at 8MHz as it does at 16MHz, but
    // it's really up to you depending on your project)
    Serial.begin(38400);

    // initialize device
    Serial.println("Initializing I2C devices...");
    accelgyro.initialize();

    // verify connection
    Serial.println("Testing device connections...");
    Serial.println(accelgyro.testConnection() ? "MPU6050 connection successful" : "MPU6050 connection failed");

    Serial.println("Updating internal sensor offsets...");
    // -76	-2359	1688	0	0	0
    Serial.print(accelgyro.getXAccelOffset()); Serial.print("\t"); // -76
    Serial.print(accelgyro.getYAccelOffset()); Serial.print("\t"); // -2359
    Serial.print(accelgyro.getZAccelOffset()); Serial.print("\t"); // 1688
    Serial.print(accelgyro.getXGyroOffset()); Serial.print("\t"); // 0
    Serial.print(accelgyro.getYGyroOffset()); Serial.print("\t"); // 0
    Serial.print(accelgyro.getZGyroOffset()); Serial.print("\t"); // 0
    Serial.print("\n");

    accelgyro.setXAccelOffset(0);
    accelgyro.setYAccelOffset(0);
    accelgyro.setZAccelOffset(0);
    
    accelgyro.setXGyroOffset(0);
    accelgyro.setYGyroOffset(0);
    accelgyro.setZGyroOffset(0);
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

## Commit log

2013-06-12 Added power supply schematics
    [GNBoard.brd, GNBoard.sch]
2013-06-12 Finished schematic/layout for voltage regulator, battery status meter, power switch and RGB LED.
    [GNBoard.brd, GNBoard.kicad_pcb, GNBoard.sch]
2013-06-12 Added readme file
    [GNBoard.brd, GNBoard.kicad_pcb, GNBoard.sch]
2013-06-12 LDR and IR connectors added to schematic
    [GNBoard.kicad_pcb, GNBoard.sch]
2013-06-12 Layout for the LDR
    [GNBoard.kicad_pcb, GNBoard.sch]
2013-06-13 v0.1 finished
    [GNBoard-B_Cu.gbl, GNBoard-Edge_Cuts.gbr, GNBoard.drl, GNBoard.kicad_pcb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]
2013-06-13 Added decoupling caps
    [GNBoard.kicad_pcb, GNBoard.sch]
2013-06-13 Finished first version, added schematics
    [GNBoard-B_Cu.gbl, GNBoard-Edge_Cuts.gbr, GNBoard.drl, GNBoard.kicad_pcb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]
2013-06-13 First tests, added source code
    [GNBoard-B_Cu.gbl, GNBoard-Edge_Cuts.gbr, GNBoard.drl, GNBoard.kicad_pcb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]
2013-06-15 Added LDR board
    [4LDR_Board-B_Cu.gbl, 4LDR_Board-Edge_Cuts.gbr, 4LDR_Board.drl, 4LDR_Board.kicad_pcb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]
2013-06-17 Added caterpillar tracks
    [Caterpillar_track.scad, Caterpillar_track.stl, attach.scad, bcube.scad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]
2013-06-17 Added encoder board
    [Caterpillar_track.scad, Caterpillar_track.stl, Encoder_Board.brd, Encoder_Board.sch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]
2013-06-17 Finished encoder board
    [Encoder_Board-B_Cu.gbl, Encoder_Board-Edge_Cuts.gbr, Encoder_Board.brd, Encoder_Board.drl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]
2013-06-17 Improvements for the GNBoard
    [GNBoard-B_Cu.gbl, GNBoard-Edge_Cuts.gbr, GNBoard.drl, GNBoard.kicad_pcb]
2013-06-18 Gerber export
    [GNBoard-B_Cu.gbl, GNBoard-Edge_Cuts.gbr, GNBoard.drl]
2013-08-09 Software tests and hardware concepts
    [ArduSkyBot_chassis_v2.3.stl, Futaba-shaft.dxf, LDR_sensor_array_support.scad, LDR_sensor_array_support.stl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]
2013-08-09 Added sensor input filtering
2013-08-10 Misc improvements
    [ArduSkyBot_chassis_v2.3.stl, main.scad]
2013-08-27 More tests with the light sensor
2013-10-23 GNBot misc update
    [4LDR_Board-B_Cu.gbl, 4LDR_Board-Edge_Cuts.gbr, 4LDR_Board.drl, 4LDR_Board.kicad_pcb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]
2013-10-23 Added more info and pictures
    [Encoder_Board.brd, Encoder_Board.sch]
2013-10-24 Added a cover for the light sensor.
    [LDR_sensor_array_support.scad, LDR_sensor_array_support_cover.stl]
2013-11-06 Design improvements, directory re-structured
    [ArduSkyBot_chassis_v2.3.stl, Futaba-shaft.dxf, GNBot_chassis_v2.3.stl, Parameterized_battery_holder.scad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]
2013-11-06 Hardware improvements
    [GNBot_chassis_v2.3.stl, configuration.scad, main.scad]
2014-01-14 Updated components to allow powering with up to 20V
    [4LDR_Board-B_Cu.gbl, 4LDR_Board-Edge_Cuts.gbr, 4LDR_Board.drl, 4LDR_Board.kicad_pcb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]
2014-02-05 Working on new version. Created backup of previous design.
    [GNBoard-B_Cu.gbl, GNBoard-B_Mask.gbs, GNBoard-B_SilkS.gbo, GNBoard-Cobre.gbl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]
2014-02-06 Working in new version for the GNBoard
    [GNBoard-B_Mask.gbs, GNBoard-B_SilkS.gbo, GNBoard-Cobre.gbl, GNBoard-Comp_.gtl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]
2014-02-06 Added support for LDRs, lots of changes
    [GNBoard-B_Mask.gbs, GNBoard-B_SilkS.gbo, GNBoard-CopperBtm.gbl, GNBoard-CopperTop.gtl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]
2014-02-07 Finished preliminary design
    [GNBoard-B_Mask.gbs, GNBoard-B_SilkS.gbo, GNBoard-CopperBtm.gbl, GNBoard-CopperTop.gtl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]
2014-02-08 Finished v1.0 of the GNBoard
    [GNBoard-B_Mask.gbs, GNBoard-B_SilkS.gbo, GNBoard-CopperBtm.gbl, GNBoard-CopperTop.gtl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]
2014-02-08 Moved v0.1 to its own folder
    [4LDR_Board-B_Cu.gbl, 4LDR_Board-Edge_Cuts.gbr, 4LDR_Board.drl, 4LDR_Board.kicad_pcb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]
2014-02-09 Updated gerber files
    [GNBoard-B_Mask.gbs, GNBoard-B_SilkS.gbo, GNBoard-CopperBtm.gbl, GNBoard-CopperTop.gtl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]
2014-02-09 Resized silkscreen texts, resistor values are now shown
    [GNBoard-B_Mask.gbs, GNBoard-B_SilkS.gbo, GNBoard-CopperBtm.gbl, GNBoard-CopperTop.gtl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]
2014-02-10 Updated value of the resistors for the battery voltage monitor
    [GNBoard-F_SilkS.gto, GNBoard.kicad_pcb, GNBoard.sch]
2014-02-26 Modified LDR support to fit the new GNBoard
    [LDR_sensor_array_support.scad, LDR_sensor_array_support.stl, LDR_sensor_array_support_cover.stl, LDR_sensor_array_support_prev.scad]
2014-02-26 Improved LDR support: tuned and easier printing
    [LDR_sensor_array_support.scad, LDR_sensor_array_support.stl]
2014-03-01 Tests with the nose sensor and real time plotting
2014-03-02 Calibration tests
2014-03-03 Stored sensor fitted coeffs to file
2014-03-04 Calibrated compass measurements
2014-03-05 Implemented control of the motors from python
2014-03-05 Tested battery duration ~2h
2014-03-09 Implemented particle filter
2014-03-27 Battery measurements
2014-05-20 New version of the chassis. Two 9V batteries now fit on the bottom of the robot.
    [Futaba-shaft.dxf, GNBot_chassis_v2.4.stl, Parameterized_battery_holder.scad, Servo-wheel.scad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]
2014-05-20 Added battery holder. Some hardware tweaks for better printing
    [GNBot_chassis_v2.4.stl, Servo-wheel.scad, Servo-wheel.stl, battery_holder.scad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]
2014-05-21 Added support for frontal IR sensor
    [GNBot_chassis_v2.4.stl, Servo-wheel.scad, Servo-wheel.stl, configuration.scad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]
2014-05-22 Improved wheel tolerances
    [Servo-wheel.scad, Servo-wheel.stl]
2014-05-22 Added angle to the battery holder
    [Servo-wheel.stl, battery_holder.scad, battery_holder.stl]
2014-05-23 Adjusted space for the IR distance sensor
    [GNBot_chassis_v2.4.stl, main.scad]
2014-05-23 Increased space for the IR sensor
    [GNBot_chassis_v2.4.stl, main.scad]
2014-07-07 Added design files for visual markers
    [tag.scad, target_support.scad]
2014-07-07 Added 3D-printable files for visual markers and target support
    [angleTag.stl, old_tag.stl, tag.stl, target_support.stl]
2014-07-19 Added board layout visualizations
2014-07-19 Repository reorganization, added latest version of the GNBot platform
    [ArduSkyBot_chassis_v2.3.stl, Caterpillar_track.scad, Caterpillar_track.stl, Futaba-shaft.dxf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]
2015-06-19 logged motor curves
2015-06-19 Added larger diameter wheel
    [Servo-wheel_large.stl]
2015-07-09 Experiments on motor calibration
2015-07-20 Finished Gyro calibration procedure
2015-07-21 Added min/max motor calibration
2015-07-22 Archived motor calibration tests
2015-07-22 Generated motor speed calibration data
2015-07-22 Finished motor response curve plots
2015-07-22 Linear calibration success!
2015-07-23 Finished plotting motor response curves and gyro drift
2015-07-24 Finished calibrated rotation function
2015-07-25 Plotted motor calibration for robot with over-tightened wheels
2015-07-27 Calibrated linear velocities
2015-07-29 Added calibration data structure & General code cleanup
2015-08-03 Plotted linear speed calibration
2015-08-03 Implemented linear speed calibration
2015-08-04 Speed calibration is now averaged
2015-08-04 Logged IR sensor calibration for multiple robots
2015-08-04 Re-fitted IR distance sensor response
2015-08-15 Plotted old controller vs new self-calibration
2015-08-19 Finished IR sensor response plot
2015-08-19 Re-render of motor calibration plots
2015-08-23 Added line & arc distance calibration
2015-08-25 Measured calibration times
2015-08-27 Plotted linear speed calibration for two different surfaces
2015-09-01 Added text to the figure that describes the measurement of the right motor's velocity

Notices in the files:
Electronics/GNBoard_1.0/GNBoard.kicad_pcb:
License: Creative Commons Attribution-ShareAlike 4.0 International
